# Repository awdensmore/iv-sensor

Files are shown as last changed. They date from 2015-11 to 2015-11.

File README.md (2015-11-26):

# iv-sensor
A sensor for voltage and current measurements used in electrochemical impedance spectroscopy. Output is suitable for 3V logic level (DSPs)

###**Operation**
The purpose of this sensor is to accurately measure the current and voltage response of a battery excited by an EIS waveform. The current is measured using a transducer (U1) and passed directly to an output connected to the ADC of a DSP.

The voltage measurement is more complicated. Because the EIS signal is a ~20mV sine wave on top of a ~12V DC signal, the DC component must be removed and the AC component amplified before it is input to the ADC for digitization. This is accomplished in several steps:

1. **Determine DC component of voltage signal**: The battery voltage is measured on the low side of the transducer (I- @ U1). That signal is passed through a voltage divider (R1 / R2), after which it is passed to an external ADC via pin 2 of P1. The external DSP uses a software low-pass filter to remove the AC component, then passes the signal back to this PCB via pin 1 of P1. However, because the DSP only has PWM output (not a pure analog output), this signal needs a DAC. The DAC is built using F1 / F2, which act as a 4-pole programmable active filter. At this point the signal (FO @ pin 1 of F2) is DC and proportional to the original battery DC component, but not the same voltage. It is therefore amplified using OP1, and is now within a few mV of the original battery DC voltage (OP1-OUT @ pin 6 of OP1).
2. **Remove DC component**: The signal created by step 1 is then removed from the original signal (I-) via OP2 (OP2_OUT @ pin 6). We now have only the ~20mV AC signal.
3. **Amplification & offset**: The AC signal is amplified ~35x at OP-3, and then offset by 1.5V at OP-4 so that the signal is always positive. The final EIS voltage signal (Vo) is output to the DSP at pin 3 of P1.

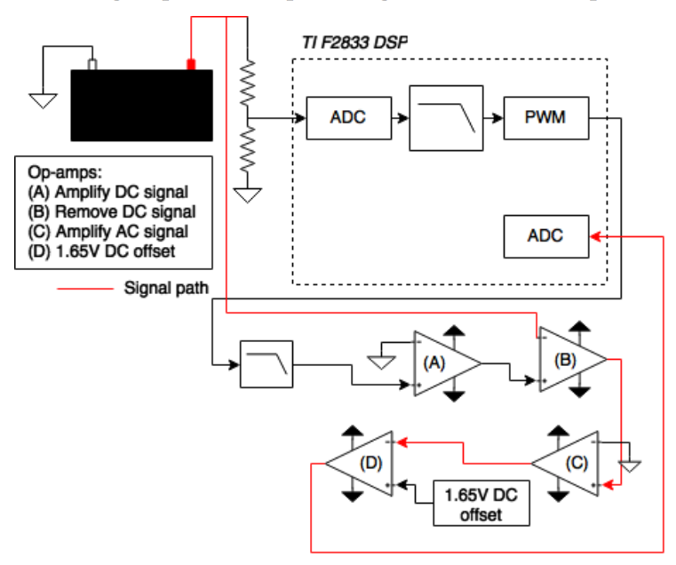
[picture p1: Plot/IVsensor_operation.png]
Sensor Operation


**Component Values**

| Component | Value |
|----------|-------|
R1 | 21.92k
R2 | 5.57k
R3 | 82.2k
R4 | 4.64M
R5 | 4.7M
R6 | 50.9k
R7 | 15.9k
R8 | 4.57M
R9 | 4.66M
R10 | 51.0k
R11 | 984
R12 | 100.1k
R13 | 19.98k
R14 | 19.98k
R15 | 100.4k
R16 | 62.3k
R17 | 62.2k
R18 | 62.1k
R19 | 62.3k
R20 | 100.0k
R21 | 2.99k
R22 | 1k
R23 | 100.3k
R24 | 22k
R25 | 21.87k
R26 | TBD
R27 | TBD
R28 | TBD
C1 - C2 | 470uF
C3 - C16 | 0.1uF

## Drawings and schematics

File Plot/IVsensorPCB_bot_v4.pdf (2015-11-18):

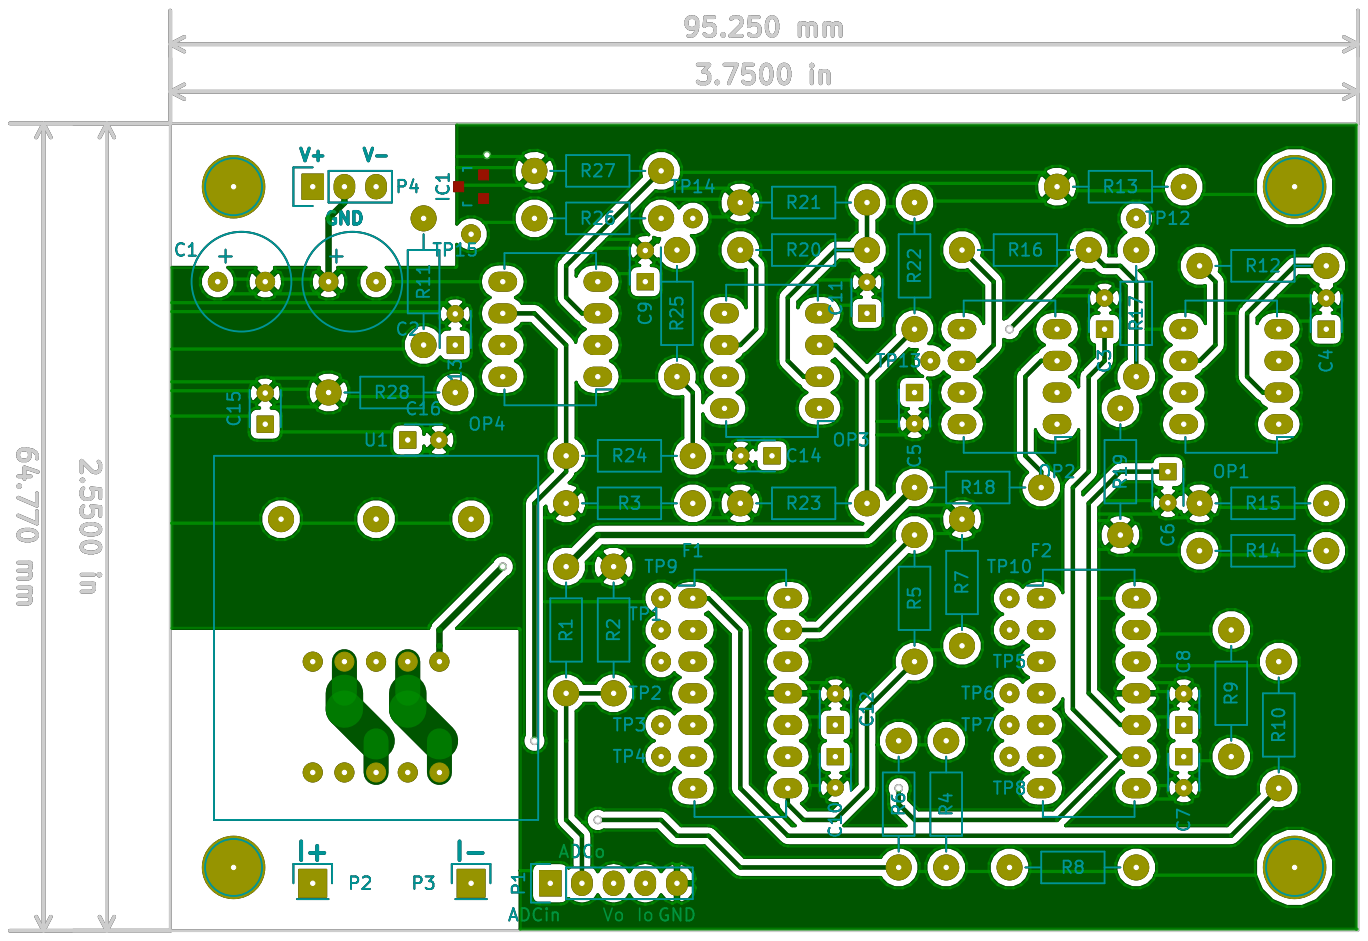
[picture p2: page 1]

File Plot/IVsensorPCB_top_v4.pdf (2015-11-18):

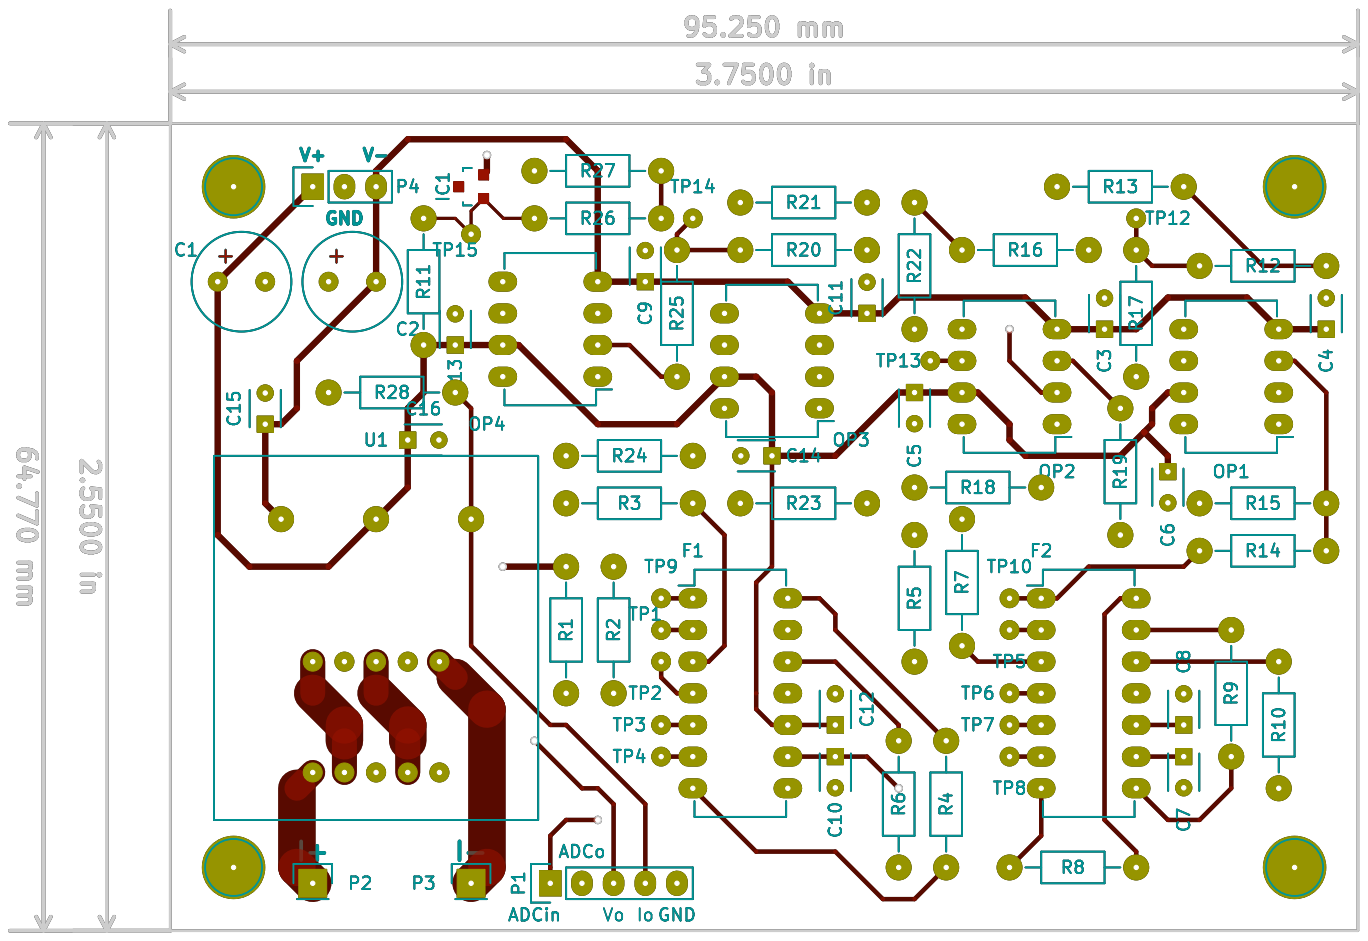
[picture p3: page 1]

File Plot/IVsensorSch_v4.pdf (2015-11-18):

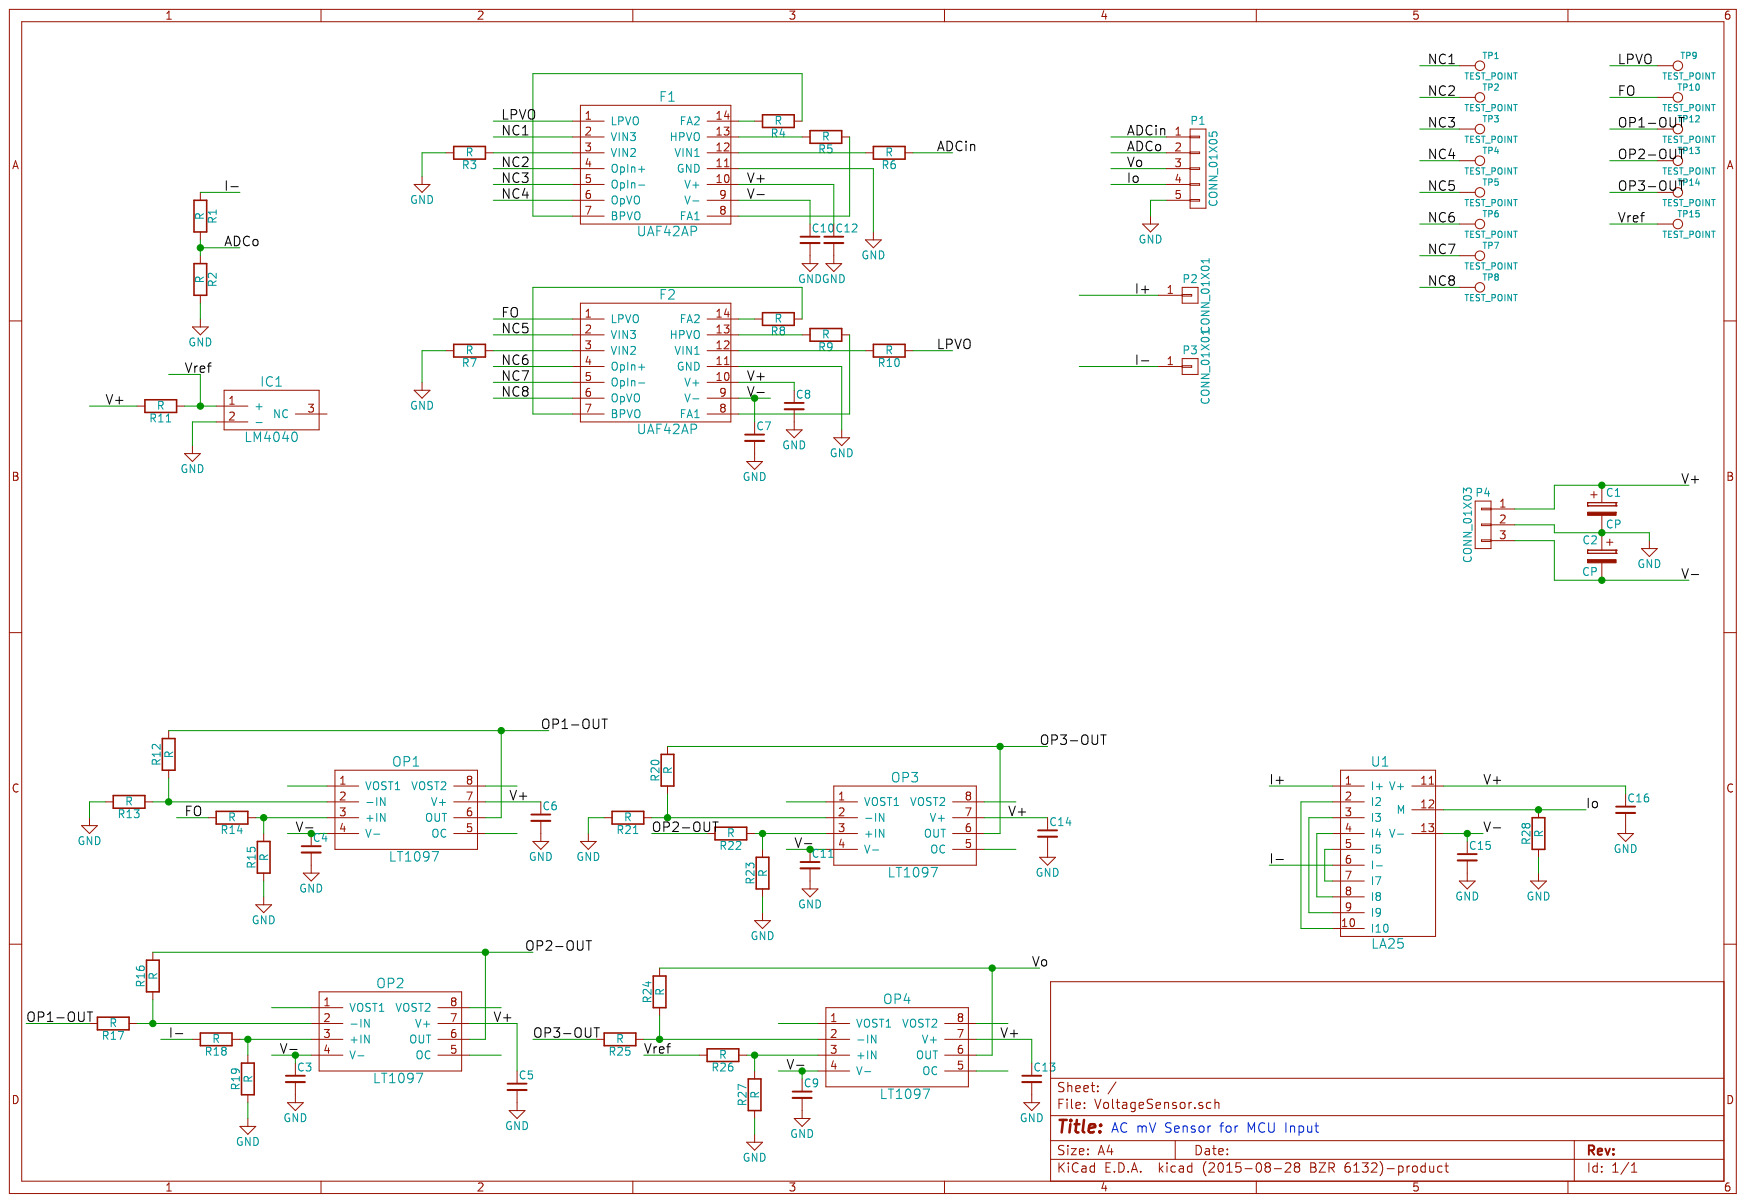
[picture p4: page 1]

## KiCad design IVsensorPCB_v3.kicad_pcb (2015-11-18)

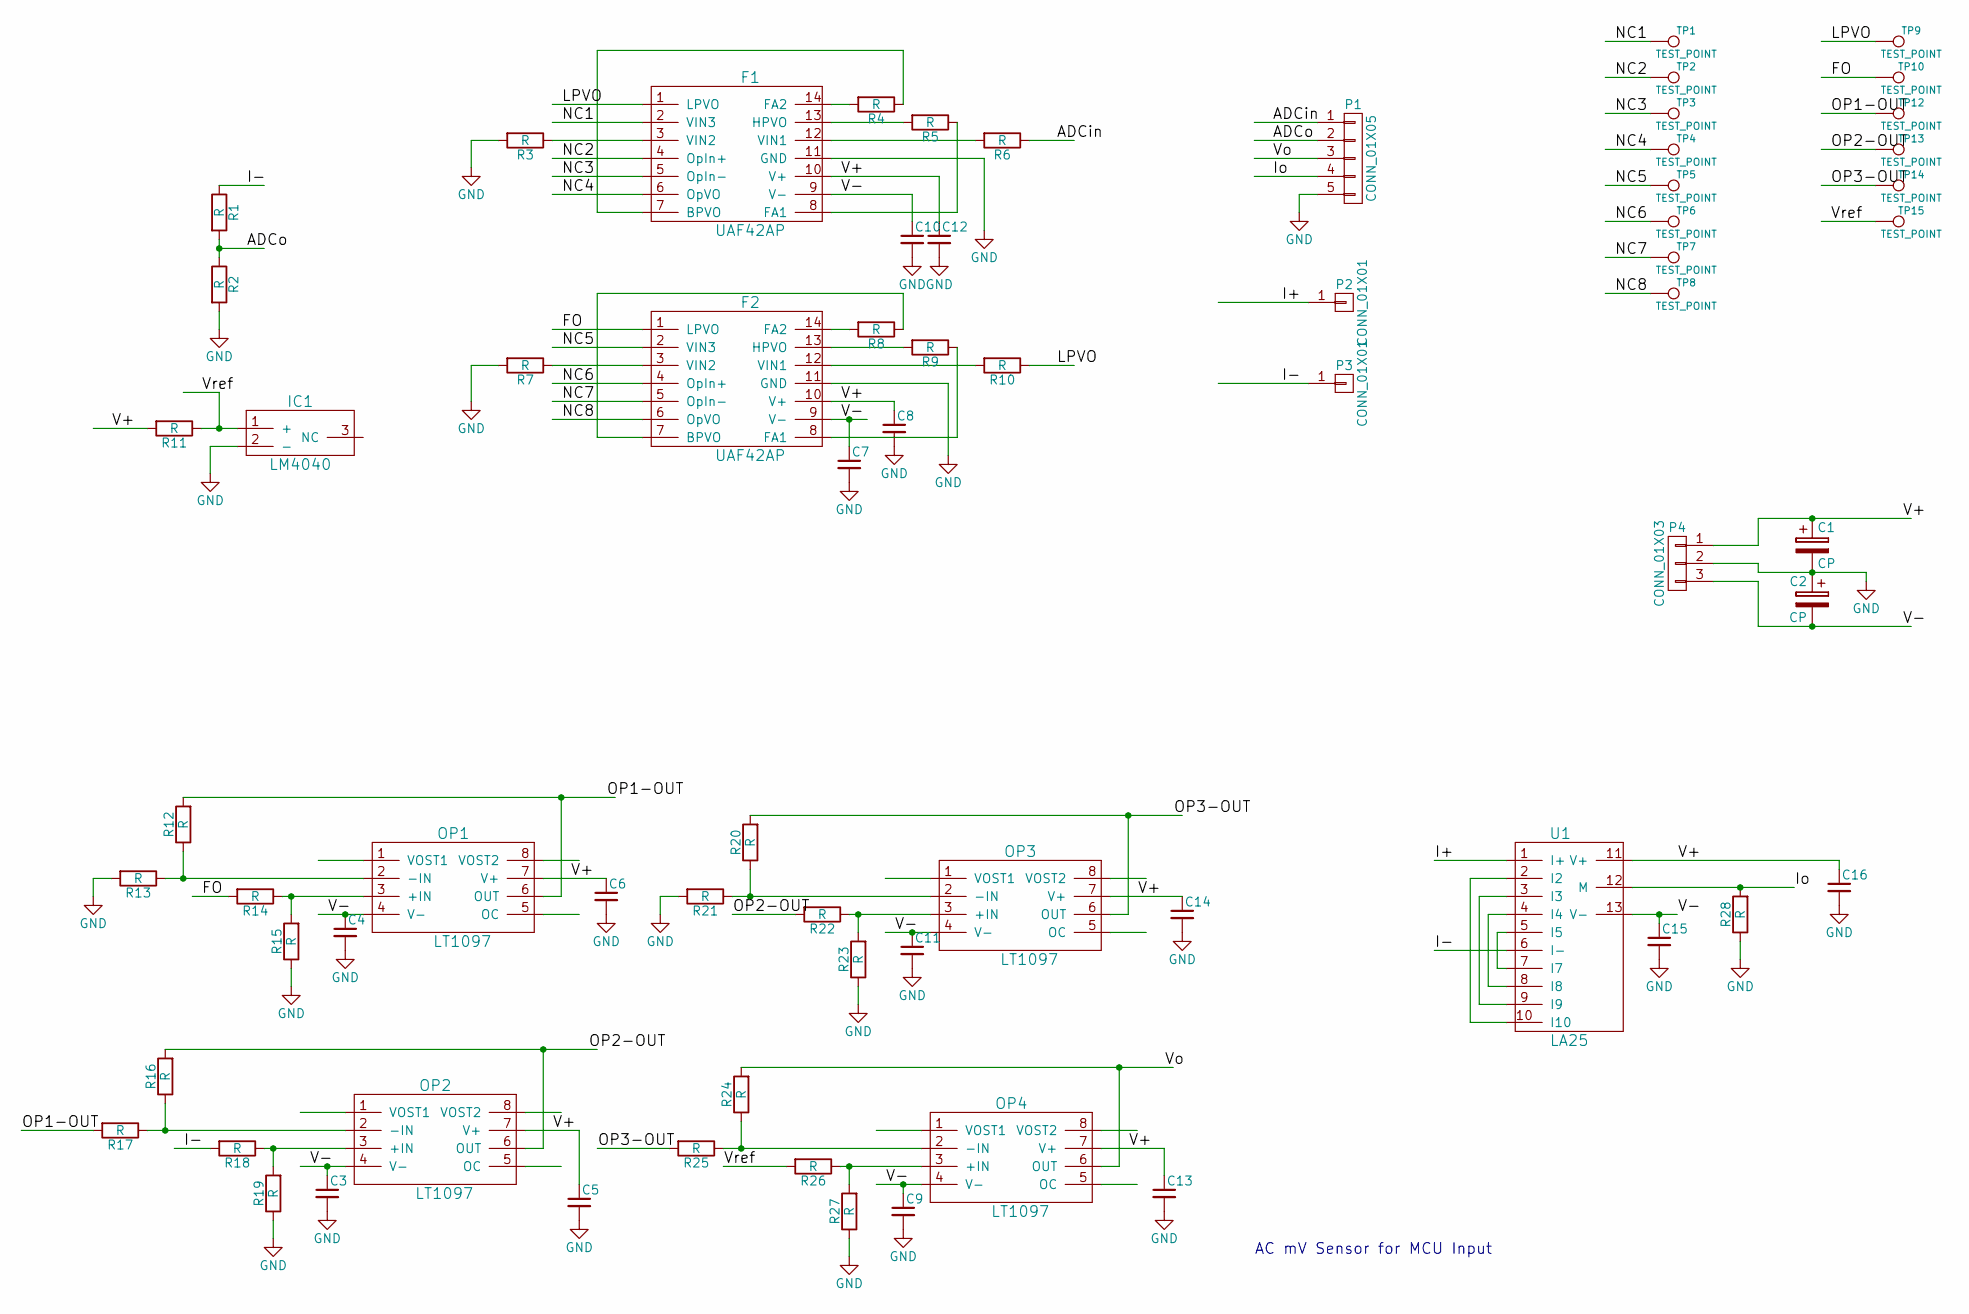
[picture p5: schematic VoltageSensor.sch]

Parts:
C1, C2: CP; Elko_vert_11.5x8mm_RM3.5
C3, C4, C5, C6, C7, C8, C9, C10, C11, C12, C13, C14, C15, C16: C_Small; C_Disc_D3_P2.5
F1, F2: UAF42AP; DIP-14_W7.62mm_LongPads
IC1: LM4040; SOT-23
OP1, OP2, OP3, OP4: LT1097; DIP-8_W7.62mm_LongPads
P1: CONN_01X05; Pin_Header_Straight_1x05
P2, P3: CONN_01X01; Pin_Header_Straight_1x01
P4: CONN_01X03; Pin_Header_Straight_1x03
R1, R2, R3, R4, R5, R6, R7, R8, R9, R10, R11, R12, R13, R14, R15, R16, R17, R18, R19, R20, R21, R22, R23, R24, R25, R26, R27, R28: R; Resistor_Horizontal_RM10mm
TP1, TP2, TP3, TP4, TP5, TP6, TP7, TP8, TP9, TP10, TP12, TP13, TP14, TP15: TEST_POINT; Measurement_Point_Round-TH_Small
U1: LA25

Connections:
/ADCin: P1.1, R6.1
/ADCo: P1.2, R1.2, R2.1
/FO: F2.1 (LPVO), R14.2, TP10.1
/I+: P2.1, U1.1 (I+)
/I-: P3.1, R1.1, R18.2, U1.6 (I-)
/Io: P1.4, R28.2, U1.12 (M)
/LPVO: F1.1 (LPVO), R10.1, TP9.1
/NC1: F1.2 (VIN3), TP1.1
/NC2: F1.4 (OpIn+), TP2.1
/NC3: F1.5 (OpIn-), TP3.1
/NC4: F1.6 (OpVO), TP4.1
/NC5: F2.2 (VIN3), TP5.1
/NC6: F2.4 (OpIn+), TP6.1
/NC7: F2.5 (OpIn-), TP7.1
/NC8: F2.6 (OpVO), TP8.1
/OP1-OUT: OP1.6 (OUT), R12.2, R17.2, TP12.1
/OP2-OUT: OP2.6 (OUT), R16.2, R22.2, TP13.1
/OP3-OUT: OP3.6 (OUT), R20.2, R25.2, TP14.1
/V+: C1.1, C5.1, C6.1, C8.1, C12.1, C13.1, C14.1, C16.1, F1.10 (V+), F2.10 (V+), OP1.7 (V+), OP2.7 (V+), OP3.7 (V+), OP4.7 (V+), P4.1, R11.2, U1.11 (V+)
/V-: C2.2, C3.1, C4.1, C7.1, C9.1, C10.1, C11.1, C15.1, F1.9 (V-), F2.9 (V-), OP1.4 (V-), OP2.4 (V-), OP3.4 (V-), OP4.4 (V-), P4.3, U1.13 (V-)
/Vo: OP4.6 (OUT), P1.3, R24.2
/Vref: IC1.1 (+), R11.1, R26.2, TP15.1
GND: C1.2, C2.1, C3.2, C4.2, C5.2, C6.2, C7.2, C8.2, C9.2, C10.2, C11.2, C12.2, C13.2, C14.2, C15.2, C16.2, F1.11 (GND), F2.11 (GND), IC1.2 (-), P1.5, P4.2, R2.2, R3.2, R7.2, R13.2, R15.1, R19.1, R21.2, R23.1, R27.1, R28.1
unnamed: F1.3 (VIN2), R3.1
unnamed: F1.7 (BPVO), R4.1
unnamed: F1.8 (FA1), R5.1
unnamed: F1.12 (VIN1), R6.2
unnamed: F1.13 (HPVO), R5.2
unnamed: F1.14 (FA2), R4.2
unnamed: F2.3 (VIN2), R7.1
unnamed: F2.7 (BPVO), R8.1
unnamed: F2.8 (FA1), R9.1
unnamed: F2.12 (VIN1), R10.2
unnamed: F2.13 (HPVO), R9.2
unnamed: F2.14 (FA2), R8.2
unnamed: OP1.2 (-IN), R12.1, R13.1
unnamed: OP1.3 (+IN), R14.1, R15.2
unnamed: OP2.2 (-IN), R16.1, R17.1
unnamed: OP2.3 (+IN), R18.1, R19.2
unnamed: OP3.2 (-IN), R20.1, R21.1
unnamed: OP3.3 (+IN), R22.1, R23.2
unnamed: OP4.2 (-IN), R24.1, R25.1
unnamed: OP4.3 (+IN), R26.1, R27.2
unnamed: U1.3 (I3), U1.9 (I9)
unnamed: U1.4 (I4), U1.8 (I8)
unnamed: U1.5 (I5), U1.7 (I7)
unnamed: U1.2 (I2), U1.10 (I10)

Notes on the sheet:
AC mV Sensor for MCU Input

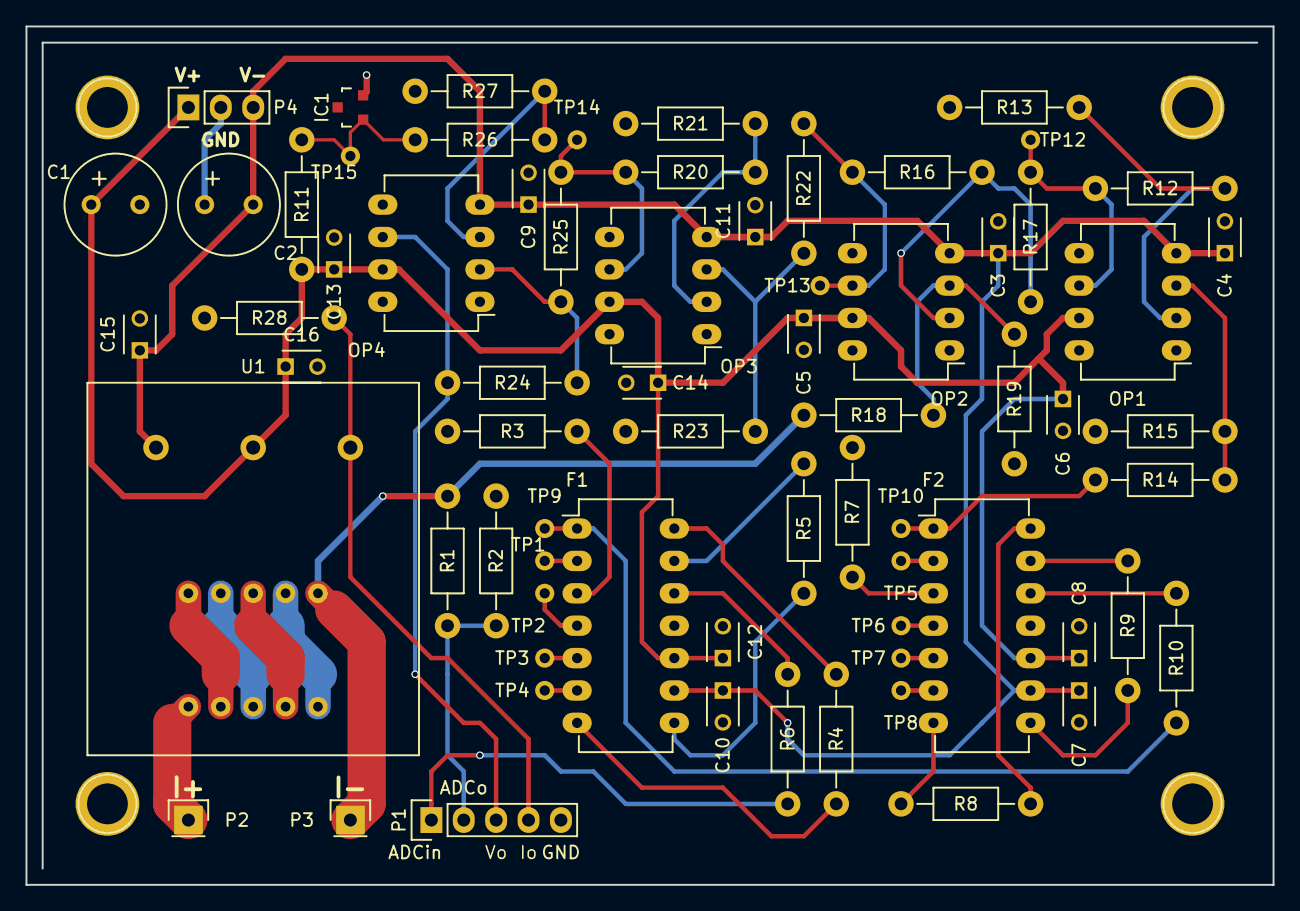
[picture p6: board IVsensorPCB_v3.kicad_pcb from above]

Board: 2 copper layers, 97.8 x 67.3 mm, 70 parts (0 on the bottom side), 47 nets.
